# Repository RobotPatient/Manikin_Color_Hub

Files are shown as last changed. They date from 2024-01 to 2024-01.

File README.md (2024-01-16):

# Manikin_Color_Hub

Welcome to the Manikin Color Hub, a part of the skin color research team RGBbaby. 
Here's an overview of our file structure:

# Manikin Colour Hub

## Led Driver Board Files, Flexible LED Strip PCBs, and Software

Welcome to the Manikin Colour Hub, a part of the skin colour research group RGBbaby. Here's an overview of our file structure:

### Arduino Spectrometer:

Contains CAD and code files for the AS7341 colour sensor. Use this sensor setup to analyze the light emitted by a specific sample.

### General Docs:

- **Product_report - individual reports:** Individual project files included in the product report.
- **Product Report:** Detailed report on our project.
- **Progress Report:** Overview of our progress.
- **Initial Questions and Answers from WKZ:** Compilation of our initial queries and responses.
- **Manual:** Comprehensive guide for our project.
- **ToDo List:** List of tasks yet to be completed.

### Led Test Setup:

Code for testing a bare neopixel LED strip in combination with an Adafruit Feather M0 Express.

### PCBs:

- **LedDriverBoardV1:** KiCad files and schematic for the first version of our LED driver board.
- **LedDriverBoardV2:** KiCad files, schematic, code, and flexible PCBs for the second version of our LED driver board.
- **LedDriverBoardV3:** KiCad files, schematic, code, and flexible PCBs for the third and final version of our LED driver board.

### Pi Spectrometer:

CAD files for the Raspberry Pi-based spectrometer.

Feel free to explore and contribute to the Manikin Color Hub's diverse set of files and resources. 
If you have questions, reach out to us!

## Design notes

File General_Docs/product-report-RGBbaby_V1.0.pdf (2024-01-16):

# Product report – RGBbaby

By Manon Sijben, Marlon Reijlink, Emiel Visser and Joris Bol

DOCUMENT ORGANIZATIONAL DETAILS:
Document Type:
Skills Consultant: | Paul van Wegen
Project Client: | Johan Korten
Education: | Embedded Systems Engineering
Institute: | School of Engineering and Automotive, Hogeschool Arnhem-Nijmegen
Report Date: | 16-1-2023
Report Version: | v1.0
Project Duration:
Education Term:
Students: | 2108100 (Joris Bol), 2111740 (Emiel Visser), 2106573 (Manon Sijben),
| 2107003 (Marlon Reijlink)

Embedded Systems Engineering · HAN University of Applied Sciences

- please don't print this document unless you really need to!

## Version management

Version | Date | Change | Name
V1.0 | 5-9-2023 | Creation document. | J. Bol
V1.0 | 26-9-2023 | Addition C4 and introduction. (detailed history) | J. Bol
V1.0 | 10-10-2023 | Changes made to requirements. | J. Bol
V1.0 | 10-12-2023 | Added more info. | E. Visser
V1.0 | 18-12-2023 | Addition C2. (detailed history) | J. Bol
V1.0 | 18-12-2023 | Addition C4. (detailed history) | J. Bol
V1.0 | 19-12-2023 | Addition C5. | E. Visser & J. Bol
V1.0 | 9-1-2024 | Added Appendix B. | E. Visser
V1.0 | 11-1-2024 | Spellcheck, added sources, small modifications. | E. Visser
V1.0 | 12-1-2024 | Spellcheck, added sources, small modifications. | E. Visser
V1.0 | 16-1-2024 | Add conclusion, addition C6, addition summary. | E. Visser & J. Bol

## Summary

This project, conducted in collaboration with Wilhelmina Children’s Hospital for HAN University of Applied Sciences, aims to develop a realistic skin that can change appearances and respond to user input. The primary objective is to contribute to a larger initiative focused on creating a lifelike doll for nurses to practice scenarios involving premature or problematic babies.

To meet the client's specifications, a comprehensive investigation into component selection was carried out. The key focus was on choosing suitable components that could alter the skin colour of the skin and a device capable of sensing when the skin is touched. The research led to the selection of the SMDLX0707RGBTR led as the skin colour altering device and the AT42QT2120-MMHR as the touch sensing device. Two PCBs were developed to mimic the functionality of the final product during this selection process.

In order to ensure a satisfactory end result, SMART-statements were defined to guide the product development. These statements were translated into a set of functional and technical specifications, aligning with the client's vision after consultation.

Following the definition of project conditions, the physical makeup of the product and software functions were outlined, using flow diagrams and schematics. The fabrication phase commenced, utilizing ECAD software for PCB development and incorporating necessary adjustments. Once the design was finalized, PCBs and corresponding components were ordered based on the preliminary research.

Upon receiving all components and PCBs, assembly took place, and the testing phase began. Unfortunately, significant issues with the PCBs emerged, leading to an inability to upload code or generate light with the led strip. Although testing became impossible, a comprehensive testing plan for potential future projects addressing the same problem was established.

While the current PCB is at this point non-functional, the research conducted holds valuable insights for future endeavours. Recommendations to rectify the issues were identified, promising enhancements for the project's utility once implemented. Collaboration with other educational sources facilitated the creation of a realistic skin, establishing a solid foundation for future innovations in this field. Despite the current challenges, the project has laid a constructive groundwork for further developments and improvements.

## Table of contents

Version management | 1
Summary | 2
1 – Introduction | 5
2 – Preliminary research – ESE | 6
2.1 – Objective and requirements | 6
2.1.1 – Objective | 6
2.1.2 – Requirements light sources | 6
2.1.3 – Requirements touch sensors | 6
2.2 – Light sources | 7
2.3 – Touch sensors | 9
2.4 – Preselection | 10
2.4.1 – Light sources | 10
2.4.2 – Touch sensors | 10
2.4.3 – Other components | 11
2.5 – Selection tests | 13
2.5.1 – Driver board | 13
2.5.2 – FlexLeds | 14
2.5.4 – Test method | 16
2.5.5 – Tests realisation | 17
2.6 – Conclusion | 20
2.6.1 – Driver board components | 20
2.6.2 – Flexible led strip components | 20
2.6.3 – Using the spectrometer | 20
3 – Functional design | 21
3.1 – Functional design | 21
3.2 – Technical specifications | 22
3.3 – User interface | 22
3.3.1 – On board interface / heartbeat | 23
3.4 – User interfacing | 24
4 – Technical design | 25
4.1 – Architecture | 25
4.2 – Interfaces | 26
4.2.1 – Power | 26
4.2.3 – Main leds | 31
4.2.4 – Microcontroller | 33

4.2.5 – User button: | 36
4.2.6 – I2C bus components | 36
4.3 – Software | 39
4.3.1 – Main structure | 39
5 – Realization | 40
5.1 – Hardware | 40
5.1.1 – I/O diagram | 40
5.1.2 – LedDriverBoard | 41
5.1.3 – Flexible PCB | 46
6 – Testing | 49
6.1 – Functional and physical tests | 49
6.2 – Software tests | 51
7 – Conclusion | 52
7.1 – Achievements | 52
7.2 – Challenges | 52
7.3 – Recommendations | 53
7.4 – Final thoughts | 53
8 – Personal evaluation | 54
8.1 – Emiel Visser | 54
8.2 – Joris Bol | 55
Appendix A – Document history | 56
Preliminary research – ESE | 56
Preliminary research – IPO | 56
Functional design | 56
Technical design | 56
Manual: | 56
Appendix B – IO diagram | 57
Bibliography | 58

## 1 – Introduction

This project is on behalf of the Wilhelmina Children’s Hospital (henceforth this will be called: WKZ). WKZ has a department specialising in premature babies or babies with problems, it is with this department we will be working the closest. WKZ wants a doll on which nurses can practise al kind of different situations. A big part of meaningful practise is meaningful feedback, small or big changes in skin hue is a large part of that.

This rapport answers the question: how we went to work to arrive at a solution and get to a satisfying conclusion. For the development process we will be following the design steps as described in the Vmodel. WKZ does not explicitly define any conditions, which is why this project is entirely defined in collaboration.

This report is made up of seven chapters, whom all individually describe an important aspect of our project. To make it possible for us to reach a conclusion, in chapter 2 (Preliminary research – ESE) there will be a lot of questions asked and answered. In chapter 3 (functional design) the function of our product will be defined in detail. Next in chapter 4 (technical design) there will be a detailed description of all our hard- and software. Chapter 5 (realisation) describes our process and struggles during the project. You can find all the tests that were conducted in chapter 6 and the conclusion in chapter 7. Chapter 7 also contains possible improvements and recommendations.

## 2 – Preliminary research – ESE

This next section is the preliminary research we did to select the leds and other components for our PCB(s).

### 2.1 – Objective and requirements

2.1.1 – Objective
This document is meant as research for the selection of components for the final product. The form factor and other product specific attributes are not discussed here. The main topics of this sub research are the selection of led or other light emitting elements and touch sensors.

We will work as follows: First and foremost, we need to select a sizeable portion of the components according to the specifications made in the following subsections in this chapter. Secondly, a cost benefit analyse will be made, taking into account the cost, component size, ease of use and feature set of the component. The component that comes out on top will be selected. If the client decides that the aforementioned component is not sufficient, the next best option will be presented.

A physical test will be conducted later in this project, if for some reason the selected component doesn’t function according to our expectations, this document will not be updated. The final component shall be mentioned in the product report.

2.1.2 – Requirements light sources
As previously mentioned, the leds or other forms of illumination must meet certain requirements.
1. It must be as flat as possible.
2. It must be as cheap as possible.
3. It must be as simple as possible (functionality mustn’t be affected).
4. It must be as energy efficient as possible.
5. It must be a SMD (Surface Mount Device) component.
6. It must be capable of at least RGB otherwise multiple different sources must be used.
7. It mustn’t generate too much heat.

2.1.3 – Requirements touch sensors
As previously mentioned, the touch sensors must meet certain requirements.
1. It must be as flat as possible.
2. It must be as cheap as possible.
3. It must be as simple as possible (functionality mustn’t be affected).
4. It must be as energy efficient as possible.
5. It must be a SMD (Surface Mount Device) component.
6. It must be able to sense pressure through the silicone.
7. Ideally it disconnects when pressed.

### 2.2 – Light sources

Type: | Description:
Link: | 19-337/R6GHBHC-A01/2T (https://nl.mouser.com/ProductDetail/Everlight/19-337-R6GHBHC-A01-2T?qs=8cKuZ6Ok2lbHoW%2FFyZa1pA%3D%3D) (Mouser, 2023)
Disadvantages: | Large surface area
Advantages: | Small, inexpensive
Price: | €0,13
Type: | Description:
Link: | WUE 150141M1731 (https://www.reichelt.nl/nl/nl/rgb-led-smd-3528-rood-groen-blauw-270-950-230-mcd-120--wue-150141m1731-p232068.html?PROVID=2809) (Reichelt, 2023)
Disadvantages: | Quite tall, expensive.
Advantages: | Bright, small surface area.
Price: | €0,46
Type: | Description:
Link: | KAA-3528RGBS-11 (https://www.tme.eu/nl/details/kaa-3528rgbs-11/led-diodes-smd-gekleurd/kingbright-electronic/?brutto=1&currency=EUR) (TME, 2023)
Disadvantages: | Quite tall, expensive.
Advantages: | Bright, small surface area.
Price: | €1,05
Type: | Description:
Link: | RND 135-00252 (https://www.distrelec.nl/nl/smd-led-rgb-plcc-468-nm-520-nm-632-nm-rnd-components-rnd-135-00252/p/30158847?cq_src=google_ads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) (Distrelec, 2023)
Disadvantages: | Quite tall, only available in large quantities.
Advantages: | Bright, small surface area, cheap.
Price: | €0,04
Type: | Description:
Link: | ILPL-K501-RGBW-SK105-01 (https://www.distrelec.be/nl/smd-led-5050-rgbw-460nm-505nm-615nm-intelligent-led-solutions-ilpl-k501-rgbw-sk105-01/p/30308082) (Distrelec, 2023)
Disadvantages: | Large surface area, expensive.
Advantages: | Bright, very thin.
Price: | €1,24

Type: | Description:
Link: | SMD-LX0707RGB-TR (https://nl.mouser.com/ProductDetail/Lumex/SMD-LX0707RGB-TR?qs=u16ybLDytRYfAsx%252BT62puQ%3D%3D) (Mouser, 2023)
Disadvantages: | Relatively expensive.
Advantages: | Very small, doesn’t use much IO, low current consumption.
Price: | €0,66
Type: | Description:
Link: | SMLP34RGBN1W3 (https://nl.mouser.com/ProductDetail/ROHM-Semiconductor/SMLP34RGBN1W3?qs=Wj%2FVkw3K%252BMB6e39pO3qaCw%3D%3D) (Mouser, 2023)
Disadvantages: | Expensive.
Advantages: | Very thin, very small, doesn’t use much IO.
Price: | €1,26
Type: | Description:
Link: | IN-P55QDTRGBW (https://nl.mouser.com/ProductDetail/Inolux/IN-P55QDTRGBW?qs=stqOd1AaK78tLn2kfF8cBA%3D%3D) (Mouser, 2023)
Disadvantages: | Large surface area, relatively expensive.
Advantages: | Thin, bright.
Price: | €0,65
Type: | Description:
Link: | CLQ6B-TKW-S1L1R1H1TBB7935CC3 (https://nl.mouser.com/ProductDetail/Cree-LED/CLQ6B-TKW-S1L1R1H1TBB7935CC3?qs=Rp5uXu7WBW8kseQbCcO3Lg%3D%3D) (Mouser, 2023)
Disadvantages: | Large surface area, relatively expensive.
Advantages: | Comes with white element, thin.
Price: | €0,85
Type: | Description:
Link: | SK6812 (3535) (https://www.digikey.nl/en/products/detail/adafruit-industries-llc/2686/5804107?s=N4IgTCBcDaIMoGkBsAOAjGAsgSQHLZAF0BfIA) (Mouser, 2023)
Disadvantages: | Still relatively large.
Advantages: | Doesn’t use much IO, low current consumption.
Price: | €0,49
Type: | Description:
Link: | WS2812b (5050) (https://www.tme.eu/nl/details/ws2812b-b/led-diodes-smd-gekleurd/worldsemi/ws2812b-black/) (TME, 2023)
Disadvantages: | Large surface area.
Advantages: | Doesn’t use much IO, low current consumption.
Price: | €0,49

### 2.3 – Touch sensors

Type: | Description:
Link: | TL3342F260QG (https://nl.mouser.com/ProductDetail/E-Switch/TL3342F260QG?qs=6C6BR4UgC3Of90YOH%2FEXyw%3D%3D&mgh=1) (Mouser, 2023)
Disadvantages: | Relatively expensive, small actuation zone.
Advantages: | Thin, relatively high actuation force.
Price: | €0,61
Type: | Description:
Link: | TS17-48-05-YE-260-SMT-TR (https://nl.mouser.com/ProductDetail/CUI-Devices/TS17-48-05-YE-260-SMT-TR?qs=tlsG%2FOw5FFgMrmlTrPhqZw%3D%3D) (Mouser, 2023)
Disadvantages: | -
Advantages: | Super thin, large actuation zone, cheap, relatively high actuation force.
Price: | €0,26
Type: | Description:
Link: | MPR121QR2 (https://www.digikey.nl/nl/products/detail/nxp-usa-inc/MPR121QR2/2186527) (DigiKey, 2023)
Disadvantages: | Discontinued, relatively difficult to integrate.
Advantages: | Small, relatively easy to control, lots of channels, stable.
Price: | ?
Type: | Description:
Link: | AT42QT2120 (https://www.digikey.com/en/products/detail/microchip-technology/AT42QT2120-MMHR/3678702) (Mouser, 2023)
Disadvantages: | Relatively difficult to integrate.
Advantages: | Small, relatively easy to control, lots of channels, stable.
Price: | €1,59

### 2.4 – Preselection

We have seen that there are a lot of different leds and sensors that we could use. To see which ones could be the best for our use case we make a preselection by putting the aforementioned parts in decision making matrixes.

2.4.1 – Light sources
For the non-addressable led strip, we choose the 19-337C_RSBHGHC-A01_2T and the WUE_150141M173100 leds in combination with standard R, G and B 0603 leds. We decide to go with these leds because they were either relatively cheap and available or very small.
Type: | Size: | Brightness: | Price: | Controllability single led: | Controllability multiple leds: | Score:
19-337/R6GHBHC-A01/2T | 6 | 3 | 3 | 5 | 2 | 19 14 14 15 15 19 12 16 16 17 17
WUE 150141M1731 | 1 | 3 | 3 | 5 | 2
KAA-3528RGBS-11 | 1 | 3 | 3 | 5 | 2
RND 135-00252 | 1 | 4 | 3 | 5 | 2
ILPL-K501-RGBW-SK105-01 | 2 | 5 | 1 | 5 | 2
SMD-LX0707RGB-TR | 6 | 4 | 2 | 3 | 4
SMLP34RGBN1W3 | 1 | 3 | 1 | 5 | 2
IN-P55QDTRGBW | 1 | 5 | 3 | 5 | 2
CLQ6B-TKW-S1L1R1H1TBB7935CC3 | 1 | 6 | 2 | 5 | 2
SK6812 (3535) | 3 | 4 | 3 | 3 | 4
WS2812b (5050) | 2 | 5 | 3 | 3 | 4
Size | Higher is better
Brightness | Higher is better
Price | Higher is better
Controllability single led | Higher is better

Table 1 Light sources

2.4.2 – Touch sensors
Because we wanted to have a good balance between buttons and capacitive touch sensors, we chose to put all but the MPR12QR2 IC on our PCBs because this IC has been deprecated since 2015. An alternative is the AT42QT2120. We have tested the TL3342F260QG and TS17-48-05-YE-260-SMT-TR buttons on our test flex PCB and the AT42QT2120 on our final flex PCB. We decided to split up the physical buttons and capacitive buttons because we wanted to do more research on capacitive touch sensors. But we couldn’t wait any longer with the ordering of the PCBs.
Type: | Size: | Actuation force: | Price: | Controllability: | Score:
TL3342F260QG TS17-48-05-YE-260-SMT-TR MPR121QR2 AT42QT2120 | 3 4 5 5 | 2 1 5 5 | 4 5 4 2 | 4 4 3 3 | 13 14 17 15
Size | Higher is better
Actuation force | Higher is better
Price | Higher is better
Controllability | Higher is better

Table 2 Touch sensors

2.4.3 – Other components
To drive the leds (addressable and non-addressable) we needed some extra hardware to drive them properly. In this section you will find which ones we choose and why.
Function: | Type: | Size: | Feature set: | Solderability: | Footprint layout: | Price: | Controllability: | Score:
IO multiplexer | PCAL9722HNMP | 4 | 6 | 2 | 4 | 4 | 3 | 23
IO multiplexer | PCA8574D | 1 | 4 | 5 | 6 | 5 | 6 | 27
IO multiplexer | PCA8575BS118 | 5 | 6 | 3 | 4 | 3 | 6 | 27
IO multiplexer | PCA9548ABS118 | 5 | 3 | 3 | 5 | 1 | 6 | 23
IO multiplexer | PCA9670BS118 | 6 | 4 | 4 | 5 | 5 | 3 | 27
IO multiplexer | PCA9536DR | 2 | 2 | 5 | 5 | 6 | 6 | 26
PWM driver | TLC5940RHBR | 4 | 5 | 4 | 4 | 4 | 6 | 27
PWM driver | TLC5947RHBR | 4 | 6 | 4 | 6 | 0 | 6 | 26
PWM driver | TLC59401RHBR | 4 | 5 | 4 | 5 | 3 | 5 | 26
PWM driver | PCA9685BS118 | 5 | 5 | 4 | 4 | 2 | 6 | 26
PWM driver | TLC59711PWPR | 1 | 4 | 5 | 5 | 1 | 6 | 22
Flash | 25LP064A-JLLE | 4 | 6 | 4 | 3 | 2 | 6 | 25
Flash | IS25WQ040-JNLE | 2 | 2 | 5 | 3 | 6 | 6 | 24
Flash | IS25LP032D-JLLE | 4 | 4 | 4 | 3 | 3 | 6 | 24
Flash | IS25WP032D-JKLE | 4 | 5 | 4 | 3 | 4 | 6 | 26
Flash | IS25LP080DJULETR | 5 | 3 | 3 | 3 | 5 | 6 | 25
Flash | IS25LP064D-JBLA3 | 2 | 6 | 5 | 3 | 1 | 6 | 23
Flash | IS25LP064D-JKLE | 4 | 6 | 4 | 3 | 2 | 6 | 25
Flash | IS25LP040EJYLETR | 5 | 3 | 3 | 3 | 5 | 6 | 25
Flash | AT25QL641-UUE-T | 6 | 6 | 1 | 4 | 2 | 6 | 25
Flash | S25FL116K | 2 | 3 | 5 | 3 | - | 6 | 19
Microcontroller | ATSAMD21J18A-AU | 3 | 6 | 5 | 4 | 3 | 2 | 23
Microcontroller | ATSAMD21J18A-MU | 5 | 6 | 3 | 4 | 4 | 2 | 24
Microcontroller | ATSAMD21J18A-CU | 6 | 6 | 0 | 2 | 2 | 2 | 18
Microcontroller | ATSAMD21G18A-AU | 4 | 4 | 5 | 4 | 4 | 5 | 26
Microcontroller | ATSAMD21G18A-MU | 6 | 4 | 3 | 4 | 5 | 5 | 27
Buffer (as levelshifter) | SN74HCT125DR | 2 | 5 | 5 | 4 | 5 | 6 | 27
Buffer (as levelshifter) | SN74HCT125RGYR | 5 | 5 | 4 | 4 | 4 | 6 | 28
Size | Higher is better
Feature set | Higher is better
Solderability | Higher is better
Footprint layout | Higher is better
Price | Higher is better
Controlability | Higher is better

Table 3 Other components

2.4.3.1 – IO multiplexer:
To detect when a user has pressed the skin, we wanted to add buttons or other pressure sensitive devices on the flexible PCBs. To register these button presses we decided to use I2C enabled IO multiplexer.

We ended up going with the PCA9670BS because the package is very small, it had all the features we wanted, it was relatively easy to solder, and the pinout was very convenient to route out to the pins on to the connector. We also found that the price was pretty low in comparison with to the other multiplexers we selected. However, there was one issue we did not pay attention to: It doesn’t have a library.

2.4.3.2 – PWM led driver:
To actually drive the non-addressable leds, we went with a specialized PWM led driver. We settled on the TLC59401RHBR led driver. This driver is small, it has a lot of features, it’s pretty easy to solder, it’s easy to route and it’s relatively cheap.

There is, however one small problem which we found out later. This chip also doesn’t have a premade library! This is why the TLC5940RHBR scores higher. Note: We have seen people use the TLC5940 library in combination with the TLC59401RHBR. We haven’t been able to verify this though.

2.4.3.3 – Flash memory:
Because we’re using neopixels we’re going to need more flash than usual. The microcontroller we’re using has 256k of memory though, so it is probably enough. But we wanted to have the option to have more if required.

We ended up choosing the IS25LP032D-JLLE because this chip is easy to solder and has enough storage. If you find the storage size inadequate, then you can replace this chip with a different chip because the pinout is more or less standardized. Note: Check the footprint very carefully because the sizes might differ. E.g. the footprint on the PCB is WSON but there are two WSON sizes 6x5mm and 8x6mm.

2.4.3.4 – Microcontroller:
To control the leds and communicate with the chips and other modules in the baby doll we will need a microcontroller.

For the test PCB we ended up going with the ATSAMD21J18A-MU because this chip has a lot of IO, but the overall footprint is relatively small.

However, there isn’t really a good Arduino board file available for this chip. This means you will either have to use the Atmel Xplained Xpro bootloader (quite limited) or the Adafruit feather M0 express bootloader (not made for this chip but will work. Extra IO can’t be used). You can also make a custom Arduino board file, but this is quite difficult. We tried using embedded C at first, but this proved too time consuming. However, it might be a good option for you.

2.4.3.5 – Level shifter:
To translate the 3.3V output signal to a voltage the neopixel leds require we need to use a level shifter. For our development board we went with the SN74HCT125DR. This chip was used in an Adafruit development board which we found adequate for our purpose.

The only downside of this chip is that it’s quite big. This is why we went with the SN74HCT125RGYR for the ledDriverBoardV3. Same chip, different footprint.

### 2.5 – Selection tests

To accurately select the correct light sources and touch sensors we decided that we are going to make a test set up consisting of a test board with all the possible functionalities and flexible test strips with the leds and buttons.

2.5.1 – Driver board
The driver board has 3 20-pin FCC connectors of which the middle eight pins are capable of input. There is a 4th FCC connector specifically for addressable leds.

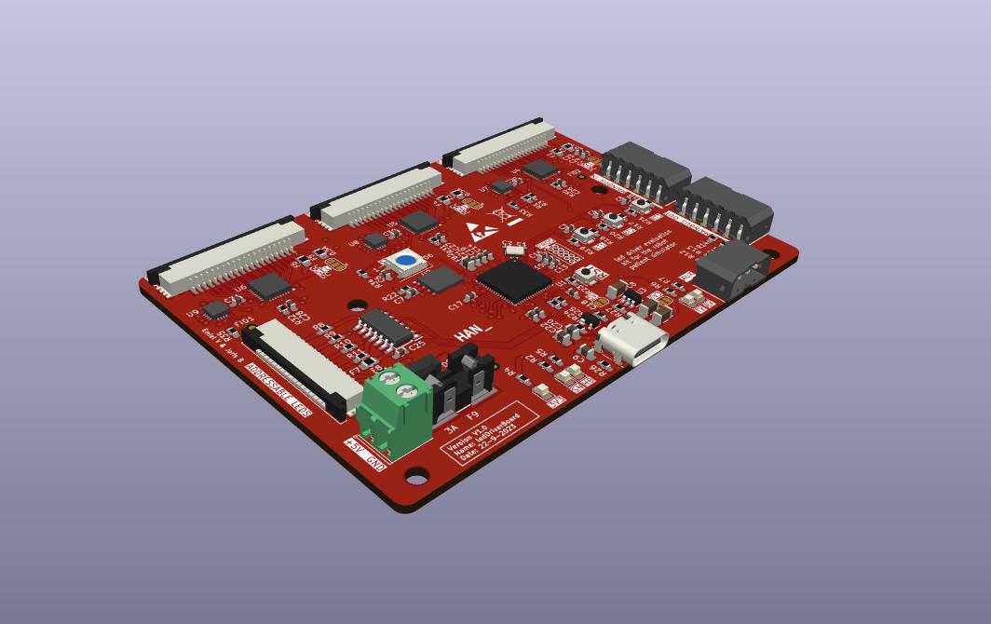
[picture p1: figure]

Figure 1 LedDriverBoardV2

This board makes use of the SAMD21J18A as microcontroller and in combination with led drivers and IO expanders the board gains a lot of functionality:

Digital interfacing
Capability: | Input/output: | Use:
3x 12-pin PWM | Output | Used to drive the normal leds.
3x 8-pin GPIO | Input/output | Used to drive the normal leds and touch sense.
4x channels for addressable leds. | Output | Used to drive the addressable leds.
debug | Input/output | Used to debug and flash the board.
Main bus in | Input | Used as the input from the mainboard.
Main bus out | Output | Passthrough.
Auxiliary | Input/output | Possibility for an extra I2C sensor.

Led functions
Colour: | State:
RGB led: Off | System is functioning normally.
RGB led: White | The PCB went into hard fault.
RGB led: Red | There is no connection between the PCB and the mainboard.
RGB led: Green | INIT finished successfully.
RGB led: Blue | The PCB is in test mode.
Heartbeat led | blinks indicating that the board is still alive.
Sens led: | Turns on when a press is detected.
3V3 led: | Is on when there is power.
Serial LEDs: | Connected to the TX and RX pins.

Button functions
Button: | Function:
RST | Resets the microcontroller.
BT1 | Can be mapped to any function.
BT2 | Can be mapped to any function.
BT3 | Can be mapped to any function.

2.5.2 – FlexLeds
The flexleds board are flexible PCBs that connect to the led driver. The two test strips that are made have the following components:

FlexLeds
Type: | Link:
Button | TL3342F260QG (https://nl.mouser.com/ProductDetail/E-Switch/TL3342F260QG?qs=6C6BR4UgC3Of90YOH%2FEXyw%3D%3D&mgh=1)
Button | TS17-48-05-YE-260-SMT-TR (https://nl.mouser.com/ProductDetail/CUI-Devices/TS17-48-05-YE-260-SMT-TR?qs=tlsG%2FOw5FFgMrmlTrPhqZw%3D%3D)
Led | SMLD12EN1WT86 (https://nl.mouser.com/ProductDetail/ROHM-Semiconductor/SMLD12EN1WT86?qs=qSfuJ%252Bfl%2Fd4fR%252B9yZydIwg%3D%3D)
Led | 19-337/R6GHBHC-A01/2T (https://nl.mouser.com/ProductDetail/Everlight/19-337-R6GHBHC-A01-2T?qs=8cKuZ6Ok2lbHoW%2FFyZa1pA%3D%3D)
Led | WUE 150141M1731 (https://www.reichelt.nl/nl/nl/rgb-led-smd-3528-rood-groen-blauw-270-950-230-mcd-120--wue-150141m1731-p232068.html?PROVID=2809)

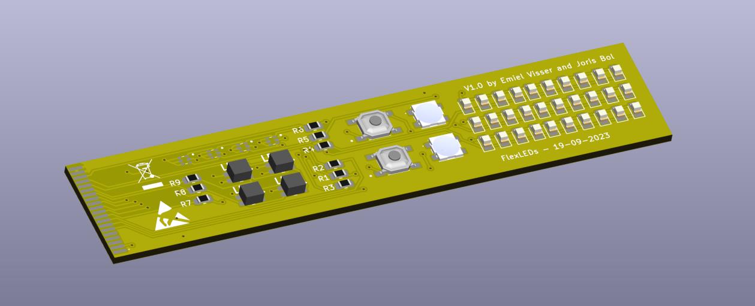
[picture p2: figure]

Figure 2 flexLeds

flexAddressLeds
Type: | Link:
Led | SMD-LX0707RGB-TR (https://nl.mouser.com/ProductDetail/Lumex/SMD-LX0707RGB-TR?qs=u16ybLDytRYfAsx%252BT62puQ%3D%3D)
Led | SMLP34RGBN1W3 (https://nl.mouser.com/ProductDetail/ROHM-Semiconductor/SMLP34RGBN1W3?qs=Wj%2FVkw3K%252BMB6e39pO3qaCw%3D%3D)
Led | SK6812 (3535) (https://www.digikey.nl/en/products/detail/adafruit-industries-llc/2686/5804107?s=N4IgTCBcDaIMoGkBsAOAjGAsgSQHLZAF0BfIA)

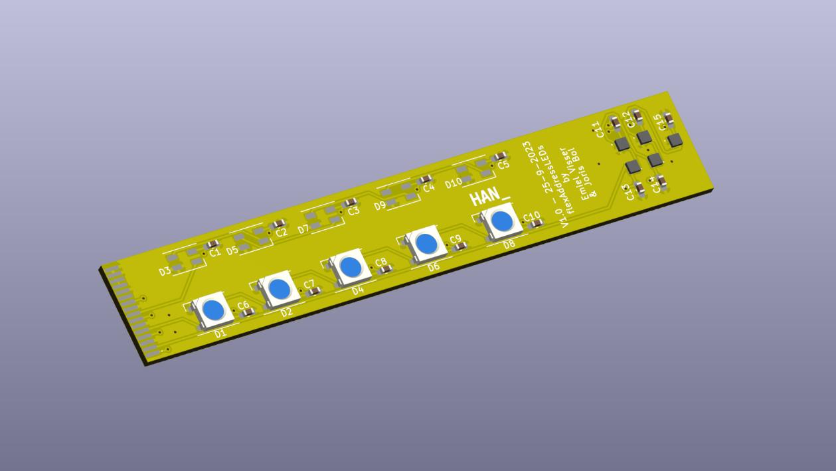
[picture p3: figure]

Figure 3 flexAddressLeds

2.5.4 – Test method
Accurate tests must be done objectively. A way to do this in our case is to measure the light intensity and the light spectrum. This can be done by using a combination of a spectrometer and a lux measuring device.

The way we intent to use these devices is as follows:

The test bench will consist of four components: the sample housing, the sensor housing, the light source, and the medium being tested. These four objects will be layered as illustrated in the figure below.

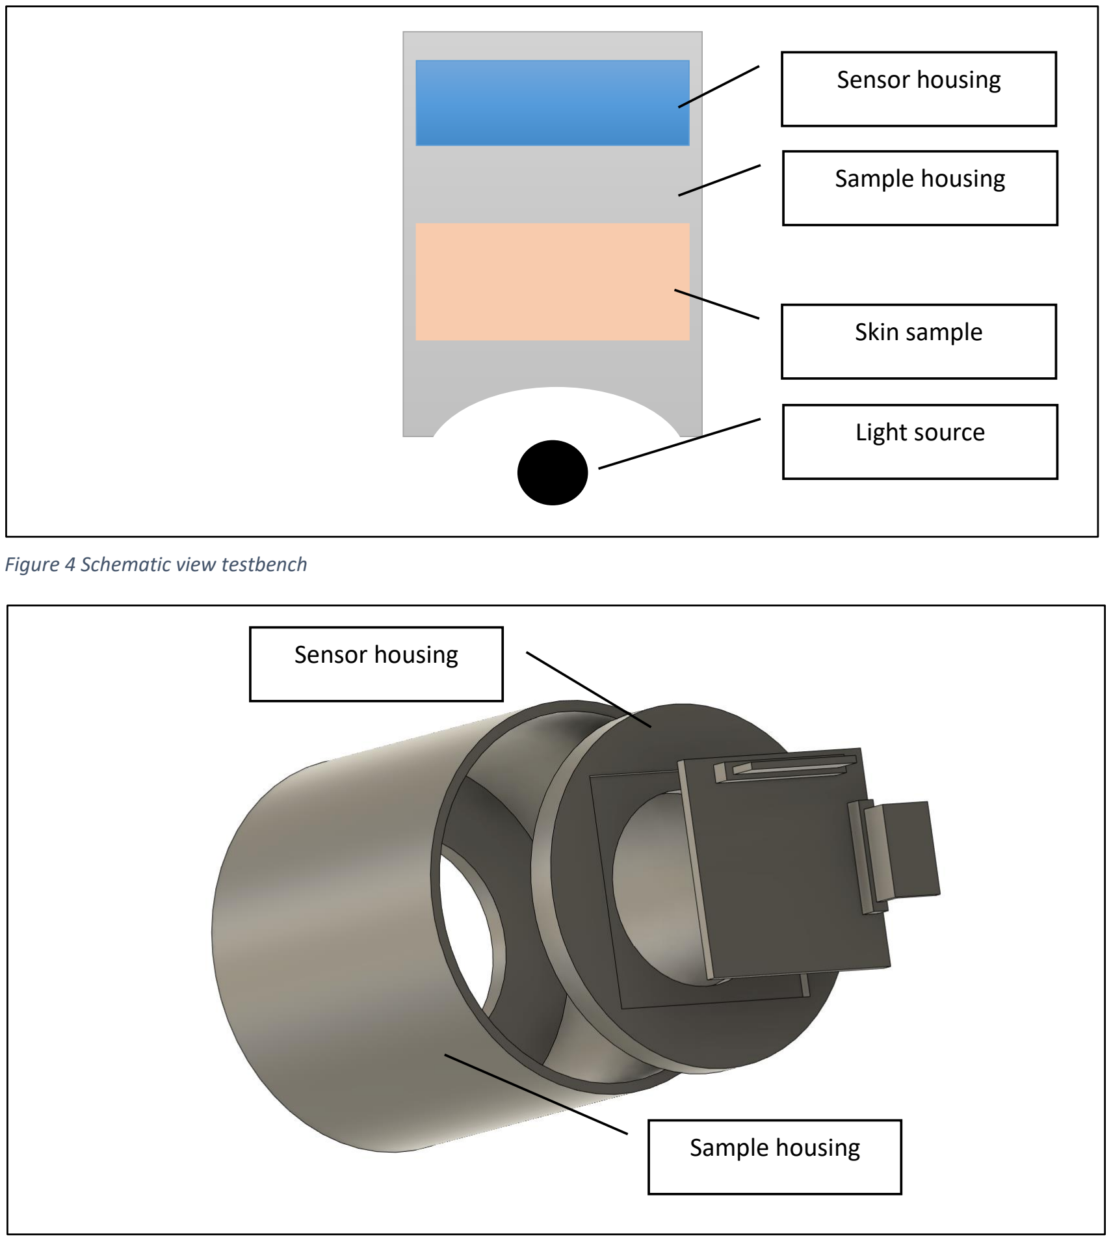
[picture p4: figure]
Figure 4 Schematic view testbench; Sensor housing; Skin sample; Sample housing; Light source

Figure 5 3D view testbench

The reason that we need to use this enclosure is to ensure that outside light is not a factor in our tests.

The components that will be used are:

- | PiCamera | (provided)
- | Spectrometer | (provided)
- | RICOH HF16HL-1b | (provided by school)
- Raspberry pi 4 or higher

For each test, the test will be conducted as follows:

1. A new sample will be put in the housing. These samples are labelled: A1, C2, etc. the samples are also labelled based on the time of production.
2. The sensor housing with the spectrometer will be lowered onto the sample.
3. The sensor and sample housing will be put on a light source.
4. The sensor value will be noted along with the sample id.
5. The sensor housing with the LUX measuring devise will be lowered on the sample.
6. Step 3 and 4 will be repeated.
7. The sample is removed from the housing.

The combination of testing and consulting will get us an objective answer on the question what colour the skin must be and what colours it must turn.

2.5.5 – Tests realisation
To conduct the test, we need to first accomplish the following steps:
1. Assemble the test board.
2. Assemble the flexible led strips.
3. Assemble the spectrometer.
4. Have working code for the spectrometer.
5. Have working code for the test board.

Each of the aforementioned points had a lot of complications and compromises, the changes that we made are all discussed in the next subchapters. At the end of this chapter, a new test plan will be established, and the coinciding tests will be carried out.

2.5.4.1 – Assembling the test board:
During the assembly end physical testing of the board, three main problems came up: the flash chip (did not line up with its footprint), the diode (that protects the board from reverse plugins) and the crystal.
- The flash chip did not correctly line up with the footprint we had chosen for the test board. At first it seemed that it did line up, but when we plugged in the test board the 3.3V led stayed of, meaning we had a short somewhere in our circuit. After some measurements we concluded that it was the flash chip end consequently removed it. This fixed the short problem.
- The diode we selected for the reverse plugin protection for the external power supply, didn’t physically fit on the board, so we bridged it and called it a day.
- The problem regarding the clock had us stumbled the longest. When we first put an Arduino bootloader on the board and noticed that nothing worked, we concluded rather quickly that it was due to the clock. But rather than fix the clock issue we tried to use bare C to program the microcontroller. This worked initially, we got some leds to blink. All the uploading, however, went via a Segger directly connected to the chip. The next step to see if our board was capable, is to see if we could get our onboard neopixel to blink. This, however, did not go as smooth as we had hoped. To use a neopixel you need to be able to generate a signal that is capable of switching H->L or L->H withing 90ns. We could not get this to work because our board was running on 8KHz instead of the 48MHz it is capable of. To remedy this, we tried to link the internal oscillators in such a way that we could generate close to 48MHz (as seen in the figure below).

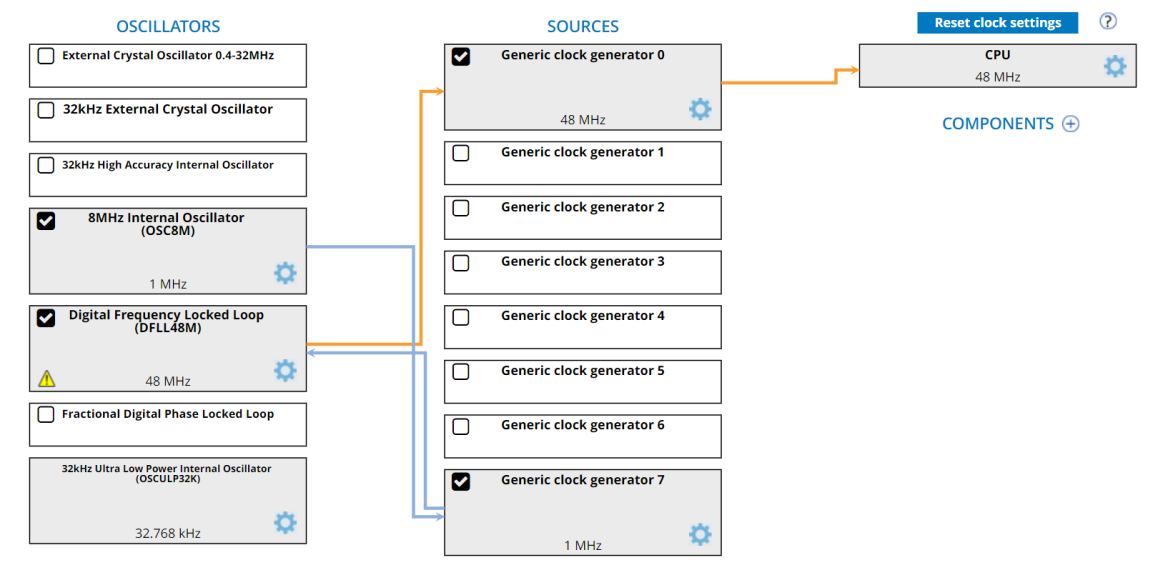
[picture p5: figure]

Figure 6 Internal clock configuration of the samd21j18a

We eventually succeeded in this and using bare C we were now capable of generating a signal with a high enough frequency. This frequency – sadly – was not capable of sustaining anything
you | could | call | stable, | so | this | also | ended | in | a | dead | end.
So we decided to combat the problem at its roots, we fixed the oscillator. The original problem was that we did not have the correct load capacitor values (C1 and C2).

2.5.4.2 – Assembling the flexible led strips:
Luckily, there weren’t a lot of problems regarding the assembly of the flexible led strips. There were however two small inconveniences. Some of the components of the led strip with the non-addressable leds came in late, so we couldn’t yet assemble them. One of the leds on the addressable led strip caused a short underneath by its pads. This however was a quick fix.

2.5.4.3 – Assembling the spectrometer:
Assembling the spectrometer was a job without too many complications. The project that we followed did not mention which raspberry pi we needed so at first, we had a pi 3 and the software did not work on it. Then we tried the pi 4 and that worked fine.

To mount the spectrometer, we had to develop a stand, shown in the figure below.

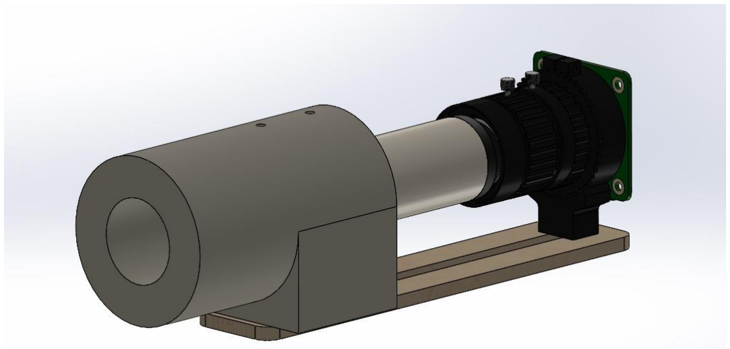
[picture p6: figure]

Figure 7 Spectrometer stand.

We assembled the spectrometer according to a process better described in the RGBbaby manual.

2.5.4.4 – Spectrometer code:
As previously mentioned, we followed a project for the spectrometer. For a more detailed inside, please refer to our manual or go directly to: https://github.com/leswright1977/PySpectrometer2 (Wright, 2023)

2.5.4.5 – Test board code:
The test board has the bootloader from the Atmel Xpro on it. This bootloader matches the SAMD21J18A pinout the best. With Arduino we can now get the leds to light up any colour we want. The previous statement only applies to the addressable leds. This is because the pins for the PWM driver don’t match up with the bootloader. This is, however, not an issue because we realised that the final product will always use some kind of addressable leds. The code that we used is from Adafruit’s neopixel lib. We can use statements like strip.fill(colour, z, n); to change the colour of the strip. This simple functionality is enough for the tests we will be conducting.

### 2.6 – Conclusion

Concluding our research, we want to achieve / know which components and methods we are going to use from now on. The things we have discovered and have the perseverance for are:

- What components we are going to use for the driver board.
- What components we are going to use for the flexible led strip.
- How future groups can use our spectrometer.

2.6.1 – Driver board components
Due to the problems, we encountered with assembling and using the test board, we will make the following changes to the newer iterations.
- We are going to use the SAMD21G18 instead of the SAMD21J18. This is due to the problems we have with addressing and using all the pins that we have available, and the fact that we don’t need as much IO.
- We dropped the support for non-addressable leds. This includes: the 20 pin FFC connector, the IO extenders, and PWM chips.

We also made some changes to existing parts of the chip, which didn’t work properly or weren’t sufficient.

- We adjusted the footprint and location of the debug connector, so it fits properly.
- The new board will support more flexible led strips.

2.6.2 – Flexible led strip components
We were able to select the ledsthat we will be using from now on. These will be the SMDLX0707RGBTR. We made this decision based on the following properties:
- They are small 0.7X0.7 inch.
- They use the same data protocol as neopixels, which is well documented.
- The don’t use a lot of power.

As for the touch detection. We tried the buttons, but they were all not able to deliver the desired result. So, we abandoned that way of detecting touch.

2.6.3 – Using the spectrometer.
The spectrometer will be more useful in later stages of this project. Sadly, we weren’t able to use the spectrometer to its fullest potential. This is why we recommend that future teams will use it. A guide can be found in our RGBbaby manual.

## 3 – Functional design

### 3.1 – Functional design

The primary function of our product is to introduce a variation in skin colours. The following list of functional requirements has been defined in consultation with our client. This list consists of three columns: The requirement number, prioritization based on the MoSCoW method and formulation of the requirement according to the SMART method.

With the MoSCoW method we can determine the importance of each specification. The M stands for must have. We must implement this specification in our final product. The S stands for should have. denoting features that are highly desirable and expected in the final product. The C stands for could have. suggesting optional features that may be considered for inclusion. The W stands for won’t have. indicating that these features won't be incorporated into the final product due to their perceived difficulty or lack of importance.

The SMART method dictates that each specification must be formulated according to the following guide rules:
- Specific: Goals should be clear and specific.
- Measurable: Goals should have measurable criteria for tracking progress.
- Achievable: Goals should be realistic and attainable.
- Relevant: Goals should be relevant to your overall objectives.
- Time-bound: Goals should have a defined timeframe or deadline.

Using the SMART method helps ensure that goals are well-defined, achievable, and aligned with your larger objectives, increasing the likelihood of success.

Functional specifications
# | MoSCoW | Description

F1 | M | The skin should be able to change colour realistically.
F1.1 | M | The skin must be able to turn yellow.
F1.2 | M | The skin must be able to turn red.
F1.2 | M | The skin must be able to turn dark blue.
F1.3 | M | The skin must be able to turn pale.
F1.4 | S | The skin shouldn’t emit a lot of light.
F1.5 | S | The skin should be able to accurately simulate petechiae. Added on 10-10-23
F2 | S | The skin should feel realistically.
F2.1 | S | The skin should not feel sticky.
F2.2 | S | The flexibility of the skin should match the flexibility of real skin.
F3 | S | The skin should look realistically.
F3.1 | S | The skin shouldn’t enter the uncanny valley*.
F3.2 | S | The colour of the skin should be realistic.
F4 | C | The skin could react to being touched.
F4.1 | C | The touched spot could display capillary refill**.
F5 | S | The system should work on different skin colours.
F5.1 | S | White skin colour.
F5.2 | S | Brown skin colour. Removed on 10-10-23
F5.3 | S | Dark brown colour. Removed on 10-10-23
F6 | M | We must test our system on different skin colours.
F6.1 | S | White skin colour.
F6.2 | S | Brown skin colour. Removed on 10-10-23
F6.3 | S | Dark brown colour. Removed on 10-10-23

*Used in reference to the phenomenon whereby a computer-generated figure or humanoid robot bearing a near-identical resemblance to a human being arouses a sense of unease or revulsion in the person viewing it.

**The 'capillary refill' time is the time it takes for colour to return to a distal capillary network after pressure has been applied.

### 3.2 – Technical specifications

The table below presents the technical specifications, adhering to the same formatting principles we applied to the functional specifications table in paragraph 1.

Technical specifications
# | Moscow | Description

T1 | M | The used microcontroller is the SAMD21J18A-M. Removed on 4-12-2023
T1.1 | M | The microcontroller must be placed on a PCB designed by us.
T2 | M | The used silicone is Eurosil 8 or 33 Transparant.
T2.1 | M | The silicone must be used to create the skin for the baby.
T2.2 | M | The silicone must not tear apart.
T3 | M | The used pigments come from NEILL’s.
T3.1 | M | X gram of pigment is used for one litre of silicone.
T3.2 | M | X gram of flocking material is used for one litre of silicone.
T4 | M | The code must be written in CPP.
T5 | S | We should make use of flex PCBs.
T5.1 | C | We could use FFC connectors.
T5.2 | C | We could use x number of buttons.
T5.3 | C | We could use leds.
T5.3.1 | S | We should supply the leds separately with power.
T6 | M | The system must be modular.
T6.1 | M | The control PCB must be detachable from the main system.
T6.2 | M | The flex PCBs must be detachable from the control PCB.
T7 | M | The control PCB must be connected to the main I2C bus to the rest of the system.
T7.1 | M | There must be two I2C ports. An input and output port.
T7.2 | M | The standard I2C protocol must be used.
T8 | M | The PCBs must be made as compact as possible.
T9 | M | The system must produce as little heat as possible.
T10 | S | The status of the PCB must be made visible to the user.

### 3.3 – User interface

A user interface (UI) serves as the medium through which a user interacts with a system or application. Examples of user interfaces include physical screens, on-screen applications, or even a basic indicator like a led, all of which enable users to engage with a machine or software.

In the following paragraph, we will detail the specific types of user interfaces we intend to use in our project, elaborate on the information they will present to the user, and outline our implementation strategy.

3.3.1 – On board interface / heartbeat
We intend to communicate vital information regarding our system's operation using six leds. These leds will serve as intuitive indicators, providing users with a clear understanding of the system's status.

In the following paragraph, we will explain the specific roles of these leds and describe how they can be effectively utilized to monitor the system's condition.

3.3.1.1 – Serial leds:
The Serial leds are designed to provide a visual representation of both the RX (Receive) and TX (Transmit) signals between the microcontroller.

These leds will be placed next to each other. We did this to maintain a good overview of the serial communication status.

3.3.1.2 – Heartbeat led:
As the name suggests, this led blinks like a heart to indicate that the board is still ‘alive.’ The led will turn on and of every second.

3.3.1.3 – Sense led:
The sense led turns on when one of the buttons is pressed. This is extremely helpful while debugging.

3.3.1.4 – RGB led:
The RGB led indicates the state of the PCB. The distinct colours indicate the following states:
Colour: | State:
Off | Nothing is wrong, PCB is off.
White | The PCB went into hard fault.
Red | There is no connection between the PCB and the main board.
Green | INIT finished successfully.
Blue | The PCB is in test mode.

3.3.1.5 – 3V3 led
The 3V3 led indicates when a 3.3 volt is present. This means that when the board is connected to power, the led turns on. This is not dependent on the chip.

### 3.4 – User interfacing

The system will interact with the user in a before specified manner, but not only the user will have impact. Our board will be largely controlled by another piece of hardware and software. This interaction is by touch in case of the user and by I2C in case of the other hardware.

A UML use case diagram is shown below, it describes what actions can be taken and how our system will react to them. In our case there are two primary actors, both depicted on the left.

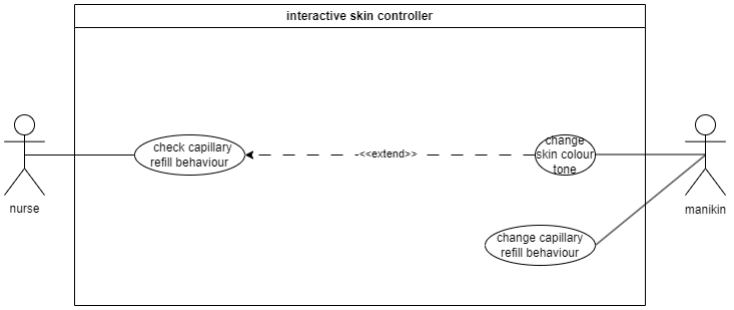
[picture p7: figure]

Figure 8 UML use case diagram

## 4 – Technical design

About the exact reason why we choose these sensors and actuators we would like to point you to our preliminary research.

### 4.1 – Architecture

In figure 1 a diagram is shown showing how our system will be controlled. The boxes contain one or more items which the board will interface with. The arrows between the boxes and board indicate the direction of the data/energy flow. The protocol/voltage is placed on the arrow.

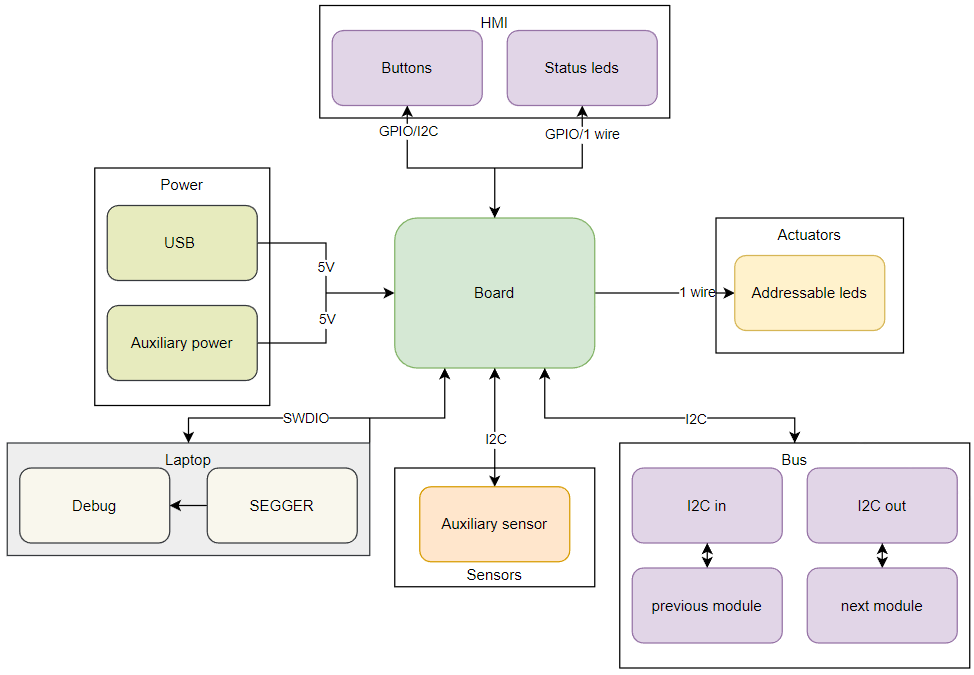
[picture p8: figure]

Figure 9 System interconnections

### 4.2 – Interfaces

In this paragraph all of the interfaces between the board and the items are described. An overview of the interfaces and items can be seen in figure 1.

4.2.1 – Power
In this paragraph the power section of our system will be described.

4.2.1.1 – USB-C:
To deliver power and upload code to our board we have added a UCB type C port to our PCB. We have added two test points so that the USB protocol can be debugged if necessary. The USB termination resistors are placed in the main sheet and are there to reduce ringing on the USB data lines. An ESD protection diode protects the host (e.g. a laptop) from ESD. The USB C port can deliver a maximum of 3A in this configuration.

Note: Don’t come close to this maximum though because the traces coming out of the port might not be able to handle 3A!

Requirement supports T7:

Specification 1.1:

No software scheme for mounting holes and fiducials.

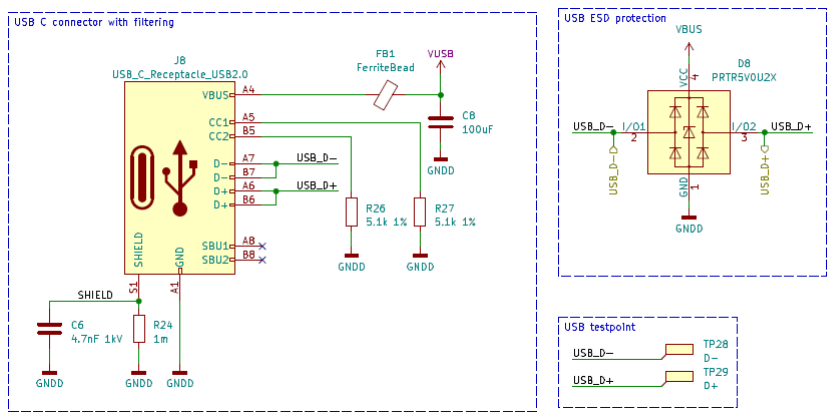
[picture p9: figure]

Specification 1.2:

4.1.1.2 – Auxiliary power:
A USB C plug can be quite bulky, so we decided to add another way of powering the system. That’s way we added a JST-XH port where 5V power can be fed into the system. We also added a fuse holder. We recommend using a fast blow fuse to protect the system in an overcurrent event.

Note: The maximum current for prolonged periods is about 2.5A. For short periods 3A is possible.

Requirement supports T7:

Specification 2.1:

No software scheme for aforementioned element.

Specification 2.2:

4.1.1.3 – 3.3V regulator:
We have decided to go with an AP2112K type regulator. This regulator drops the auxiliary and/or USB voltage down to 3.3V which is used by the microcontroller and other components. The regulator is decoupled using three decoupling capacitors and will deliver 3.3V when 5V is applied to its input.

Requirement supports T7:

Specification 3.1:

No software scheme for aforementioned element.

Specification 3.2:

4.2.2 – Status leds:
We have integrated multiple leds onto the board to provide users with clear visual indicators for various processes taking place on the controller board. These leds serve as a user-friendly interface, offering real-time feedback on the ongoing activities and status of the system.

4.2.2.1 – Status led (neopixel):
We have opted for the SK6812MINI neopixel led due to its compact package size. Additionally, these leds offer significant IO savings, a crucial factor because we decided to go with the ATSAMD21G18 instead of the original ATSAMD21J18 microcontroller. Another compelling reason for choosing this specific led is its compatibility with the existing protocol we are using for other leds. This not only streamlines our development process but also minimizes the need for additional code, promoting efficiency and consistency across our lighting system.

Requirement: supports T10

Specification 4.1:

Specification 4.2:

4.2.2.2 – HB led (heartbeat):
The Heartbeat led blinks at a fixed frequency. In the event that this led stops blinking, it indicates a system crash or that the system is stuck in a loop. Typically, a system reset is the recommended solution to address such issues.

Requirement supports T10

Specification 5.1:

Specification 5.2:

4.2.2.3 – Health led:
This led will be on when the board is in good health. And will turn of when the board encounters errors that it can’t handle properly.

Requirement supports T10

Specification 6.1:

Specification 6.2:

4.2.2.4 – Voltage indicator leds:
We've added voltage indicator leds on the board for a quick check on the availability of the two supply voltages.

Requirement supports T10

Specification 7.1:

No software scheme for aforementioned element.

Specification 7.2:

4.2.2.5 – Receive and transmit leds:
To give the user an indication if the serial bus is working, we have added a TX and RX led.

Requirement T10

Specification 8.1:

No software scheme for aforementioned element.

Specification 8.2

4.2.3 – Main leds
We have found that the SMD-LX0707RGB-TR leds fit our requirements.

Requirement T5.3

Specification 9.1:

Specification 9.2

4.2.3.1 – Neopixel output drivers:
To convert the 3.3V microcontroller output signal to a 5V output signal which results in a more stable signal. We have chosen the SN74AHCT125RGYR buffer IC. In our tests we have used the SN74AHCT125DR. the RGYR version has a smaller package which is why we went with this version for our latest revision. Every in- and output has a test point.

Requirement supports T5.3.

Specification 10.1:

No software scheme for aforementioned element.

Specification 10.2:

4.2.3.2 – FFC/FPC flat cable connectors:
To connect the flex PCBs to our control PCB we are using 16pin FFC/FPC connectors. We are using 1A resettable fuses on the 5V and 3.3V power rails. The 62-ohm resistors are there to prevent ringing on the data lines. We have also opted to breakout an I2C bus to pin 11 and 12 on the connector which enables a next group to add a I2C enabled device to be used on the flex PCBs. We also decided to breakout two IO’s to pin 8 and 9 on the connector. The user can use the for general purpose applications.

Note: The connector only makes contact on the under side so if you want your parts to be on top of the flexible PCB you need to place the connector on the underside!

Requirement T5

Specification 11.1:

No software scheme for aforementioned element.

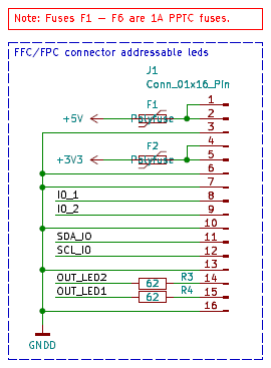
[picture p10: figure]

Specification 11.2:

4.2.4 – Microcontroller
We have chosen the ATSAMD21G18A microcontroller. This microcontroller is used by the Adafruit feather M0 express board which makes integration with Arduino or some other platform a lot easier.

Requirement T1

Specification 12.1:

The software for the microcontroller is the combination of the other specified software schematics.

Specification 12.2:

Note: The decoupling capacitors and filtering for the MCU can be found in the Power sheet of the schematic.

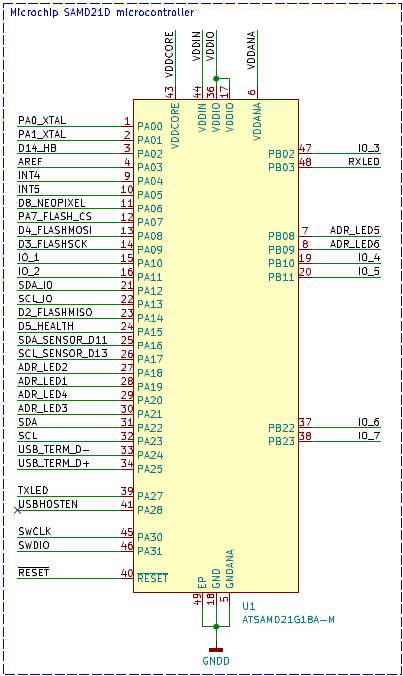
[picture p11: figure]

4.2.4.1 – Clock:
The SAMD21G18A runs on a 32.768mHz clock crystal. C1 and C2 are load capacitors. These are crucial for getting the correct clock speed. If you end up going with a different clock crystal, you will probably need te recalculate the load capacitors. The formula is in the schematic. But this formula is incorrect. For the correct formula have a look at paragraph 5.1.2. You can verify the clock speed at the test points we have placed on the clock pins.

Requirement supports T1

Specification 13.1:

No software scheme for aforementioned element.

Specification 13.2:

4.2.4.2 – Flash memory:
We are using a 64kb flash chip. The chip communicates via SPI. Every communication pin has been connected to a test point making debugging easier.

Requirement general functionality

Specification 14.1:

Specification 14.2:

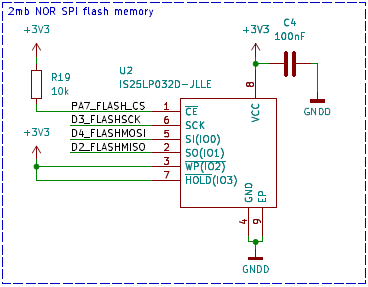
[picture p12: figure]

4.2.4.3 – Debug header:
If you want to write software to the chip (e.g. flashing a bootloader) you can use this port with a programmer like the J-LINK mini edu. This port can also be used to debug the processor and peripherals. We have added test points on the reset and data lines just in case.

Requirement general functionality

Specification 15.1:

No software functions for debug header.

Specification 15.2:

4.2.4.3 – Reset button:
To reset the system, we can use the physical reset button.

Requirement general functionality

Specification 16.1:

No software schemes for reset button.

Specification 16.2:

4.2.5 – User button:
We had one IO left so we routed that to a button. This button also has a test point.

Requirement general functionality

Specification 17.1:

Specification 17.2:

4.2.6 – I2C bus components
There are three I2C busses available. All I2C busses have test points.

4.2.6.1 – Main bus:
The main bus is the communication bus that communicates with other modules in the baby doll. The main bus has two ports. Main bus in and main bus out. You should connect the output cable of the previous module to the main bus in port on the PCB INT4 is connected to main bus in. The main bus out port connects to the next module. INT5 is connected to this port.

Requirement T7

Specification 18.1:

Specification 18.2:

5.2.6.2 – IO bus:

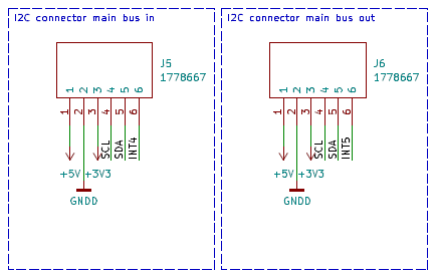
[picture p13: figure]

We wanted to maintain the possibility to add other I2C enabled devices to the flex PCBs. This is why we have broken out one I2C bus to every FFC/FPC connector. This bus also has test points.

Requirement supports T6

Specification 19.1:

See specification 18.1.

Specification 19.2:
Note: I2C output pins can be found in paragraph 4.2.3.2 – FFC/FPC flat cable connectors

4.2.6.3 – Auxiliary bus:
This bus is meant for auxiliary sensors. This bus does not have an interrupt pin connected to it and the output voltage is 3.3V only. We have used a JST-XH connector. We also added more test points tot the data pins.

Requirement supports T6

Specification 20.1:

See specification 18.1.

Specification 20.2:

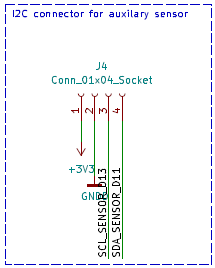
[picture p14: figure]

4.2.7 – Mounting holes and fiducials:
We have added mounting holes to the PCB the hole size is 3.2mm which means a M3 screw can be used to secure the PCB into place. The exposed copper pads near the screw hole are not connected to ground. The fiducials are positioning marks for the PCB manufacturer and pick-and-place machine.

Requirement general functionality

Specification 21.1:

No software scheme for mounting holes and fiducials.

Specification 21.2:

### 4.3 – Software

In this paragraph the software structure is described.

4.3.1 – Main structure

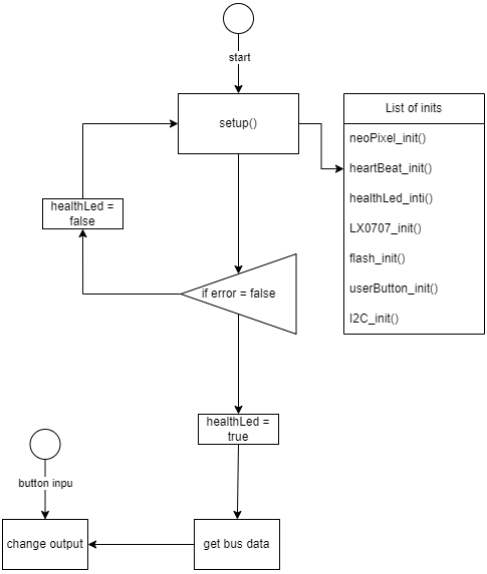
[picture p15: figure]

Figure 10 Main software structure

## 5 – Realization

In this part of the report, we describe the realisation of the project in combination with several design choices we have made to come to our final product.

### 5.1 – Hardware

In this paragraph we will describe all the hardware with relevant design choices that we have made.

We have used KiCad 7.0.9 to create the PCBs. For the 3D files we used SolidWorks 2022 and Fusion360.

5.1.1 – I/O diagram
The input/output diagram for our final PCB is listed below. In this diagram we have shown which pins are used to control the different functionalities.

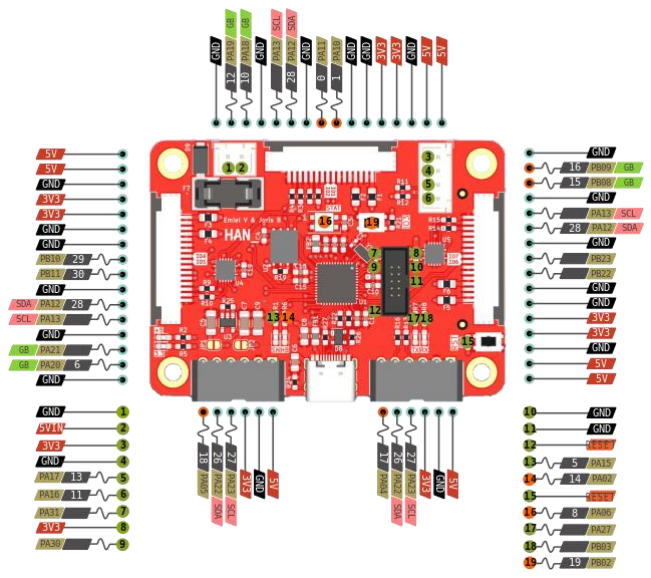
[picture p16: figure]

Figure 11 Pinout ledDriverBoardV3

For the full pin description go to: Appendix B – IO diagram

5.1.2 – LedDriverBoard
The complete schematic of the driver board for the flexible led strips is described here.

Main schematic:
In this schematic the microcontroller section is shown. We have added pullup resistors and test pads for all the I2C data busses. You can find them in the top left. The microcontroller can be found in the top middle section of the schematic. We went with the ATSAMD21G18A. As discussed in paragraph 2.4.3.4 of the preliminary research.

We have also added two buttons. A user programmable button and a reset button. These buttons have test pads as well.

If you look to the left, you’ll find the flash chip. We chose the IS25LP032D-JLLE flash chip. The reason why we chose this flash chip can be observed in paragraph 2.4.3.3 of the preliminary research.

Below the flash chip circuit, you will find the status neopixel and the USB termination resistors. The neopixel has a decoupling capacitor. It’s value can be found in the datasheet for the SK6812 led (https://www.mouser.com/datasheet/2/737/SK6812MINI_REV_01_1_2-1915201.pdf) (Mouser, 2023). The USB termination resistor values have been taken from the Adafruit feather M0 express schematic (https://learn.adafruit.com/adafruit-feather-m0-express-designed-for-circuit-python-circuitpython/downloads) (Adafruit, 2023).

Below the microcontroller you will find the mounting holes and fiducials. The mounting holes have a size of Ø3.2mm. The fiducials have no electrical purpose. They are location markings for the manufacturer.

Next to the fiducials we have placed the debug header. With this header you can debug the microcontroller and upload code or bootloaders. The pin header is a 2x5 pin header with a 1.27mm pitch.

Below that you will find the I2C bus connectors for the main bus in and out and the auxiliary connector. The Main bus in and out connectors have an extra pin connected to an interrupt enabled I/O pin. The auxiliary connector does not have this option.

Next to the auxiliary I2C connector you will find the clock circuit. You need to calculate the load capacitors for the crystal. The formula and specifications can be found in the datasheet on page 929 (https://ww1.microchip.com/downloads/aemDocuments/documents/MCU32/ProductDocuments/DataSheets/SAM-D21-DA1-Family-Data-Sheet-DS40001882H.pdf) (Microchip, 2023) and 931 (https://ww1.microchip.com/downloads/aemDocuments/documents/MCU32/ProductDocuments/DataSheets/SAM-D21-DA1-Family-Data-Sheet-DS40001882H.pdf) (Microchip, 2023)

The Clext in the formula on page 929 depends on your clock crystal, this value can be found in the datasheet of your clock crystal (https://nl.mouser.com/datasheet/2/360/file_PRODUCT_MASTER_50812_GRAPHIC03-542305.pdf) (Microchip, 2023)

The Cstray value is the capacitance of the traces going to the microcontroller and the clock circuitry in the microcontroller. This is usually around 5 or 6pF. However, the datasheet tells us that our Cstray is about 1.5pF per 12.5mm with a trace width of 0.175mm. We used a trace width of 0.25mm. The total trace length is around 8mm so a Cstray of 1.5pF should be good.

12.5pF = ([3.2pF + CLEXT] * [3.7pF + CLEXT]) / ([3.2pF + CLEXT + CLEXT + 3.7pF]) + 1.5pF

CLEXT = 18.6pF = 18 or 19pF
Note: This means the calculation and Clext (C1 and C2) in the main schematic are incorrect.

Next to the clock circuitry you will find the leds for the power indication, the TX and RX indicator leds, the heartbeat and health leds.

Above the led and clock section you will find a section with touch pads. These pads are connected to most of the IO pins and other data lines.

Above the test pad section, you will find the three FFC/FPC connectors which will connect the flexible PCBs to the mainboard. We added two I/O pins to each of the three FFC/FPC connectors. You can do whatever you want with them. We also connected an I2C bus to each of the three connectors, more on that later. The connector also has two led channels connected to it which you can use for addressable leds. Note: The led channels are 5V out!

The connectors have two 5V and two 3.3V power lines. These power lines have a 1A PPTC fuse on them. Note: Don’t run all led channels at their maximum current. The fuse will blow.

The next two squares are the power and led driver sheets. See the next paragraph.

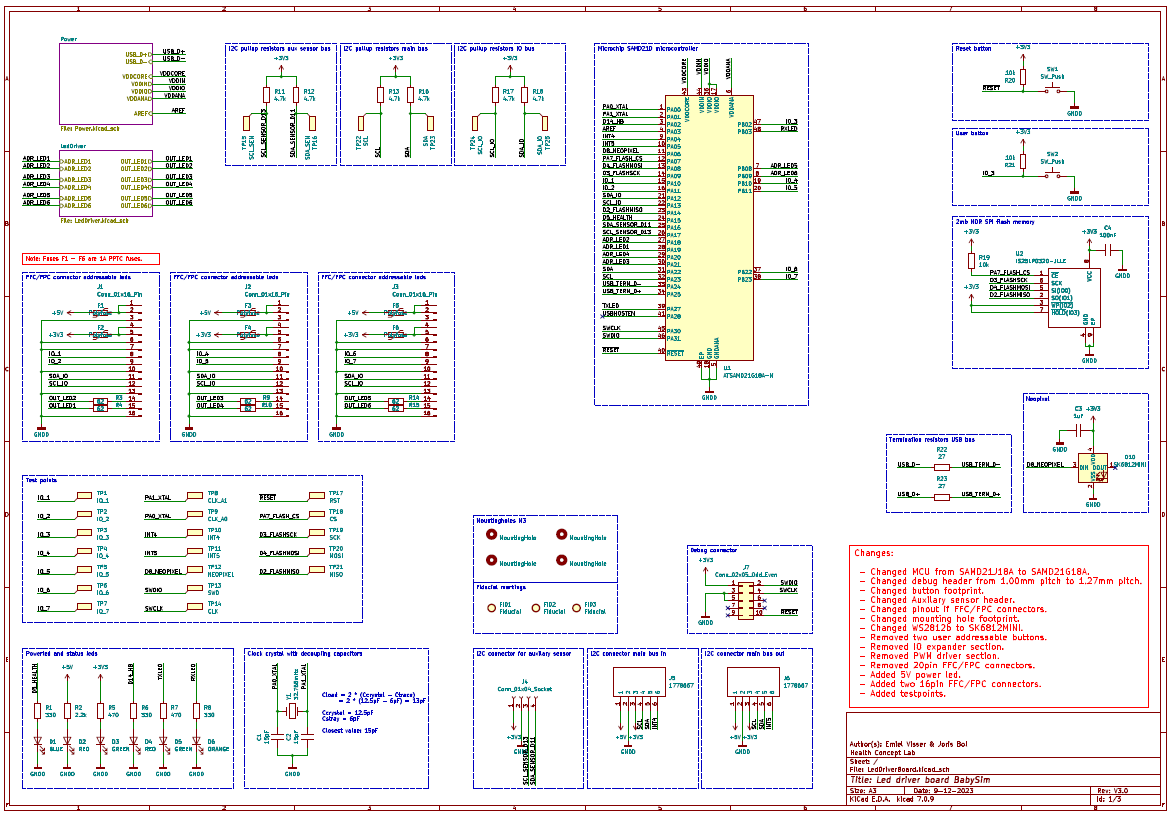
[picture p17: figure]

Figure 12 Main schematic

Power schematic:
We choose to go with a USB-C connector because the EU has begun to make the USB-C connector a legal requirement in portable devices. To make our design compliant with upcoming EU regulations, more futureproof, repairable, and thus more sustainable we decided to include this connector in our design. We added some filtering on the VUSB line. The incoming voltage is 5V@3A max. Next to the USB port circuitry you will find the ESD protection diode for the USB voltage and data lines. We also added two test points to the USB data + and USB data lines.

In this schematic you will also be able to find the decoupling capacitors for the microcontroller.

The auxiliary in connector has a 3A fast blow fuse. You can connect an external 5V power source to this connector. There is another test point connected to the connector.

The USB power lines, and Auxiliary power lines connect to the AP2112K-3.3 low dropout regulator (LDO) this LDO converts the 5V voltage to 3.3V. Be aware that the maximum output current of the LDO is about 600mA. We have added two more test points. One for 5V and one for 3.3V.

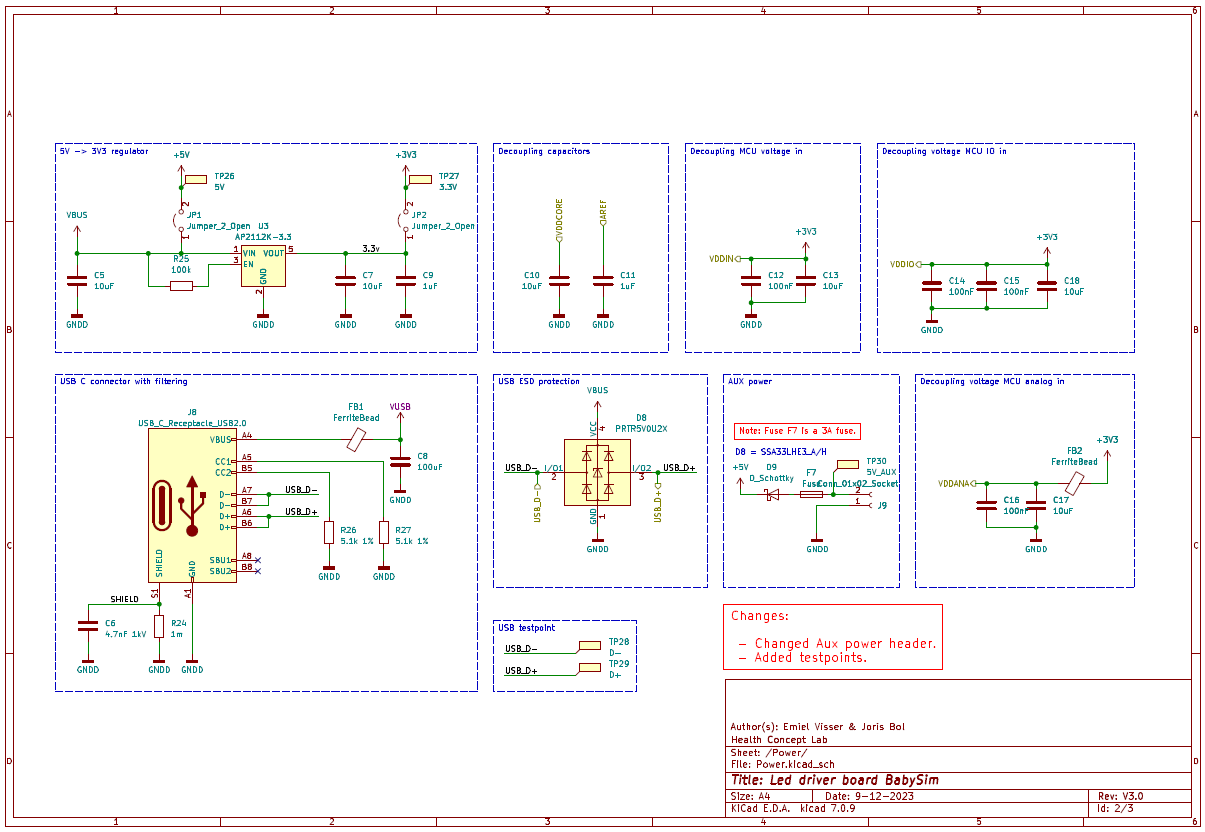
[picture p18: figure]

Figure 13 Power schematic

Led driver schematic:
In this schematic you will find the gate buffers (level shifters if you will) for converting the 3.3V led data signal to 5V. We have used the SN74AHCT125RYGR chip for this purpose. If you would like to know why we chose this particular chip. Have a look at our paragraph 2.4.3.2 of the preliminary research.

All input channels and output channels have test points on them just in case you need them.

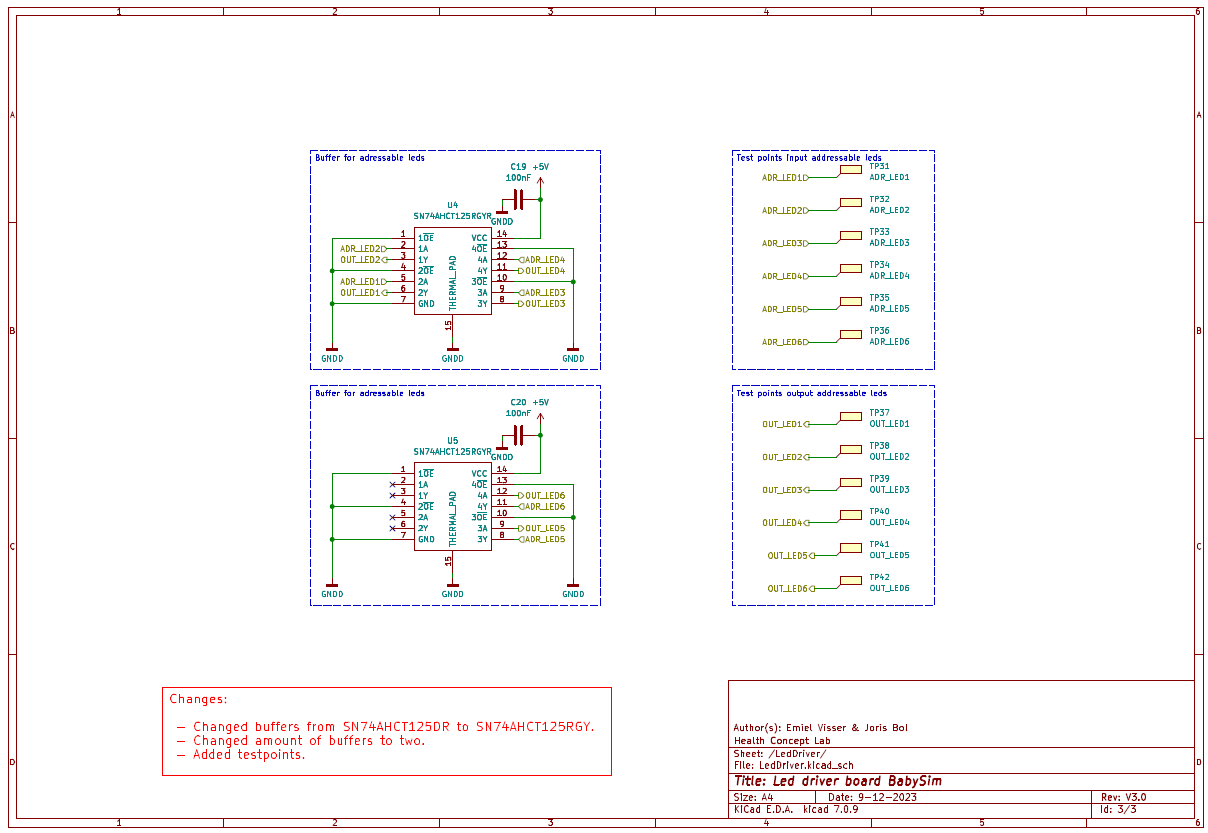
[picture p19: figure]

Figure 14 Led driver schematic.

LedDriver PCB:
Creating the layout for a PCB is always one of the hardest parts of creating a PCB design. We began by creating subgroups of components. After that we started placing the components in the subgroups in the correct orientation. We began by placing them in the PCB area. By doing this you quickly get a sense of scale.

After we had done this, we started routing the subgroups. Then we improved the component placement and updated the placement of some of the components in the subgroups. After everything was routed, we started adding the labels and logos.

For the PCB stack up we decided to go with a four-layer design. By doing this we gain a lot more room to route te traces. Going with this particular layer stack up also gives us more signal stability.

The stack up is as follows:

Layer: | Net name:
F.Cu (front) | Signal/Ground.
In1.Cu | Ground.
In2.Cu | Power 3.3V/5V.
B.Cu (Back) | Signal/Ground.

We tried to make the In1 and In2 layers a power and ground only layer, but we ended up having to route a couple of traces on these layers as well.

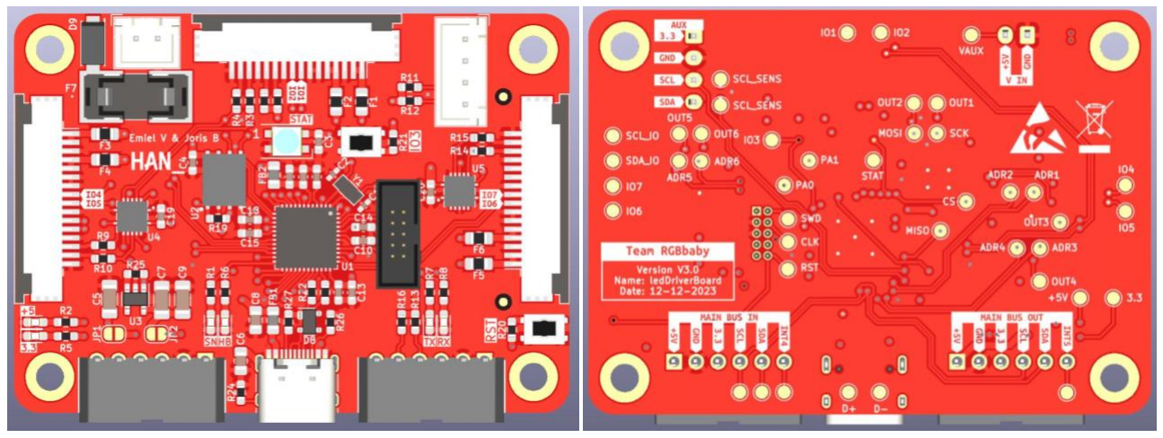
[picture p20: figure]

Figure 16 Driver board front | Figure 15 Driver board back

5.1.3 – Flexible PCB
This paragraph describes the function and considerations made during the design and assembly of the flexible PCB. This PCB is responsible for the colour changing capabilities of the skin we developed. It also contains the capability to sense touch, using a capacitive touch chip and pads. This particular part of the PCB is still in its testing face and has not been proven.

The flexible PCB consists of four main parts:

- The connector.
- The leds.
- The capacitive touch chip.
- Touch pads (which are not visible on the figure below.)

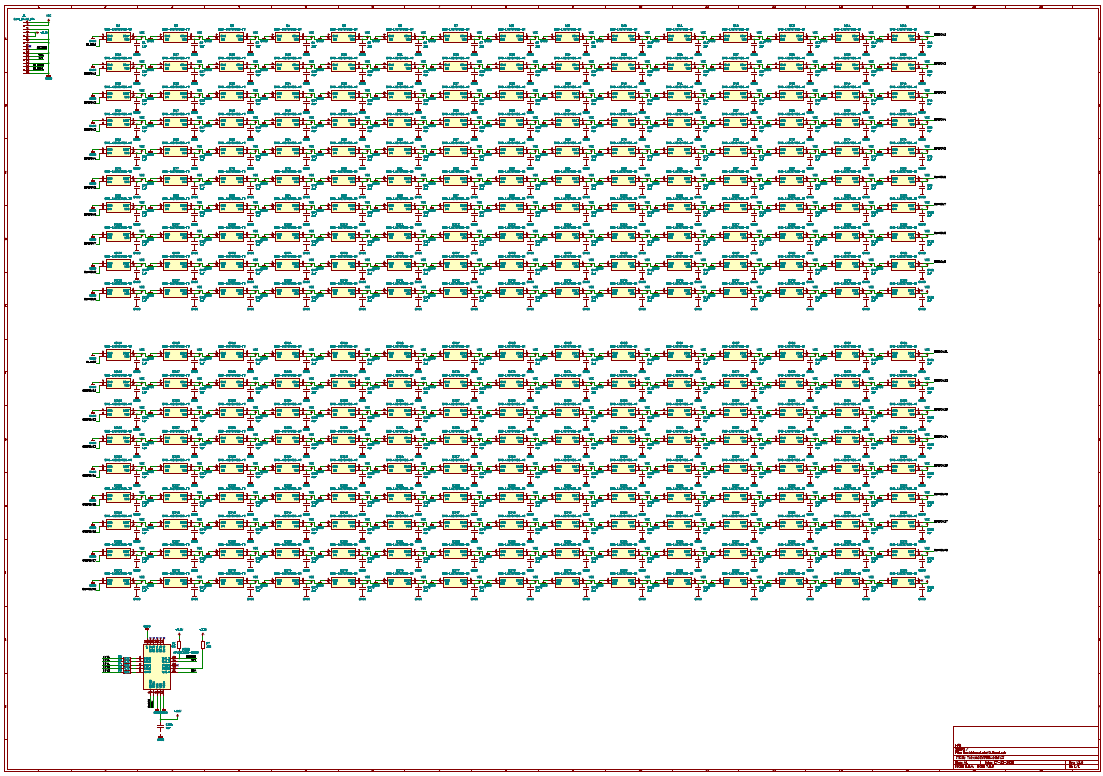
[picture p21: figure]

Figure 17 Main schematic

The connector:
The connector of the flexible PCB is not a component but rather the PCB itself. It must fit in a FFC connector, which is present on the driver board. To successfully make a piece of the PCB function as a connector we had to add traces in the correct place, and we needed to add a stiffener, so the connector does not bend or rip. The measurements and connection are depicted in the figures below.

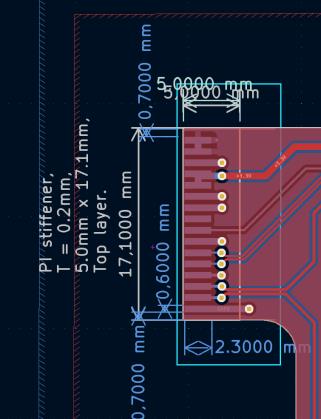
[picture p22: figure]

Figure 18 Connector schematic | Figure 19 Connector layout

The leds:
As sufficiently explained in paragraph 2.6.2, we choose the SMDLX0707RGBTR leds. these are present on the PCB in great number. The led grid contains 15 X 19 leds. this totals 285 leds. they are arranged in such a way that the leds are spaced 3,9mm centre to centre. This came out of our tests as a small enough gap, so the leds don’t cause spotting.

The leds are connected in such a way that it snakes down, starting at the left. The first 150 leds are driven by one IO pin and the other leds by another. This is because we were worried that driving all 285 leds with one io pin would exceed the maximum amount of ram we have available.

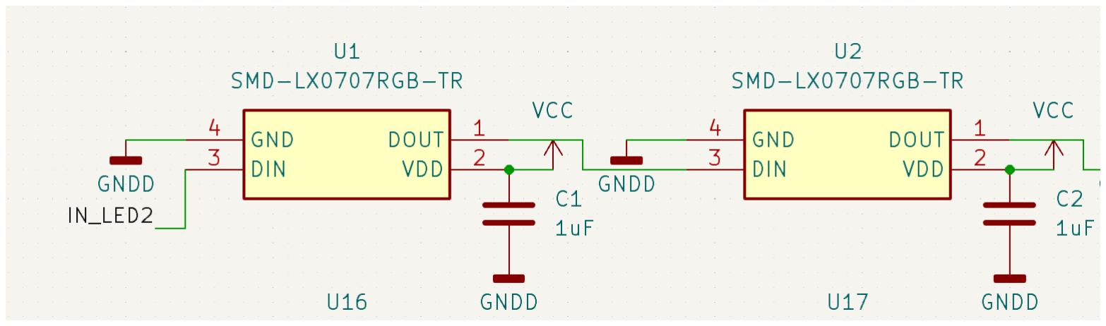
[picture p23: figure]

Figure 20 leds schematic

The capacitive touch chip:
The capacitive touch chip, which is the AT42QT2120-MMHR, is capable of sensing touch via the capacitive properties of touch. Have a look at paragraph
2.4.2 in the preliminary research to find our requirements
for the touch sensor.

It has the capabilities to run in two modes: standalone mode and comms mode. We use comms mode because we want to be able to communicate with the chip via I2C. This enables us to read the state of registers rather than relay on the multiple out channels of the chip.

We use six pins for detecting touch. Five of the pins function as a key. These keys are capable of sensing direct touch, consequently, you need to put your finger directly on the pads. The other pin is something called a prox key.
This pin – in contrast of the other keys – is capable of
sensing distance to your finger.

There is also a guard pin, which is responsible for protecting the pads for interference, more about this subject can be found in the next paragraph.

Touch pads:
The pads are responsible for supplying a surface with which you can interact. As previously mentioned, there are six pads. Five of which are keys, and one is a prox pad.

It is important to sufficiently protect the pads of interference, because of its fragile nature. We do this by using the guard channel and a ground plain.

The guard channel combats the noise that is present on the pads by putting the reverse of the interference on the guard channel. The guard channel raps around the pads so it can adequately protect them.

The ground plain is at the back side of the pads. For the pads to work correctly, there must be a precise reference point, from which the chip can derive the capacitive difference. A perfect 0V is ideal for this, hence the ground plain.

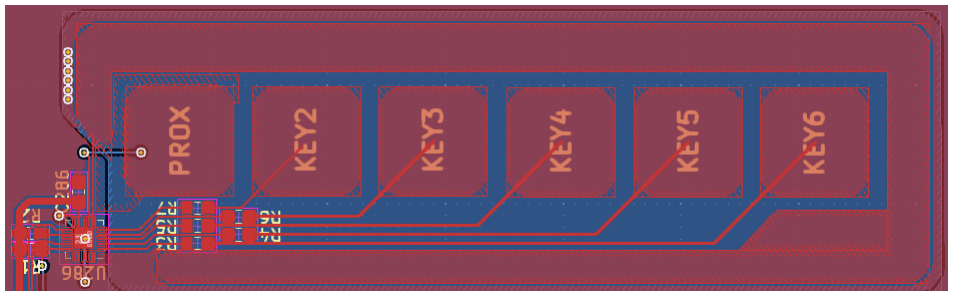
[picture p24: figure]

Figure 22 pad layout

Figure 21 Capacitive touch chip

## 6 – Testing

In this chapter we will describe the testing process and our findings. This will be done with the help of a testing method which will be described in its respective paragraph.

### 6.1 – Functional and physical tests

The Action/input variable of the test are determent by the functional an technical specifications.

Project name: RGBbaby | Date: -
Test case ID: 001 | Name: -

Function/module/program under test:

Main PCB

Test | Action/input | Expected result | Pass/Fail | Actual result
1. | The PCB turns on. | The PCB can successfully turn on. | pass | -
2. | 3V3 is available. | When 3V3 is available the corresponding led turns on. | pass | -
3. | 5V is available. | When 5V is available the corresponding led turns on. | pass | -
4. The heartbeat led is | used. | When the PCB is on the heartbeat led turns on and of with the frequency of 1Hz | - -
5. | The serial leds are used. | The serial leds turn on when there is serial communication. | - -
6. | The sense led is used. | The sense led turns on when a button is used ore when the skin senses touch. | - -
7. | The RGB led is used. | The RGB led is capable of simulating the following behaver: | - -
Colour: | State:
Off | Nothing is wrong, PCB is off.
White | The PCB went into hard fault.
Red | There is no connection

| between the PCB and the main board.
Green | INIT finished successfully.
Blue | The PCB is in test mode.
8. The PCB uses the main | I2C bus. | The PCB is capable to use the main I2C bus to read and write data. | - -
9. The PCB can generates | the data signal for the addressable leds. | The PCB can successfully generate the data signal for the addressable leds. | - -
10. The PCB supplies the | led strip with sufficient power. | The PCB can successfully supply 5V and 3V3 to the led strip. | - -
11. The PCB acts upon the | input of the led strip. | The PCB is capable of acting upon the input of the led strip, which is generated by the sense chip. | - -
Project name: RGBbaby | Date: -
Test case ID: 002 | Name: -

Function/module/program under test:

Flex PCB

Test | Action/input | Expected result | Pass/Fail | Actual result
1. The leds make the skin | turn yellow. | The skin turns a realistic yellow, without becoming a light beacon. | - -
2. The leds make the skin | turn red. | The skin turns a realistic red, without becoming a light beacon. | - -
3. The leds make the skin | turn dark blue. | The skin turns a realistic dark blue, without becoming a light beacon. | - -
4. The leds make the skin | turn pale. | The skin turns a realistic pale, without becoming a light beacon. | - -
5. One of the touch pads is | activated by a user. | We can detect and use the input of the user. | - -

6. The proximity pad is
activated by a user.

We can detect and
measure the user input.

It may be apparent that the test are incomplete and lack conclusions. This is because of the technical issues we encountered. These issues are further described in the conclusion of this rapport.

### 6.2 – Software tests

Due to the technical complications mentioned in the conclusion. We were not able to supply a sufficient software testing plan and its corresponding conclusions.

## 7 – Conclusion

Our goal was to create a solution for inducing a colour change and touch in the skin of a baby CPR doll. Our objectives included making a test setup for the components and solutions we wanted to test, writing code for controlling the driver board and documenting our findings.

### 7.1 – Achievements

Testing:
We have done a lot of research on led driving and touch sensing options. Our findings can be reused for future projects.

Hardware:
We have created a test PCB that allowed us to test different hardware and software configurations. With the lessons we learned from that test PCB we created our final PCB. This PCB has six led channels capable of driving leds up to 1A per connector. Each connector has an I2C connection so that a capacitive touch sensor can be used.

Software:
We have written a software library that makes the implementation of the led channels, IO and touch sensor a lot easier.

### 7.2 – Challenges

We have encountered a lot of hurdles, slowing us down. This is the reason why we haven’t been able to finish the project completely.

Microcontroller:
The microcontroller we had chosen for our first test board had no Arduino implementation in our configuration which meant we weren’t able to use every functionality we wanted to try out.

Clock:
On both boards we have/had problems with the onboard clock. The clock crystal needs to put out a clock frequency that is within the 32.768kHz range. However, it refused to do that on both boards which wouldn’t allow the code to be run using the Arduino bootloader because the Arduino bootloader uses the external clock instead of the internal clock circuitry. On our test board we manged to fix this by changing the load capacitors to a different value. However, this wouldn’t work on the final version.

Programming:
Because the clocks wouldn’t work we had to program in embedded C/C++. Creating libraries for the different chips is very time consuming which is what brought us into trouble. We were also unable to find a suitable Arduino bootloader for the test PCB which meant we couldn’t use a lot of the functions we wanted to test.

We also wired up the debug header to the final PCB incorrectly which meant we had to solder jumper wires to pads on the back to be able to program it.

Shorts:
We also had a number of shorts on both boards and on our led strip due to an excess amount of solder paste resulting in bridges, which took a lot of time to solve those.

### 7.3 – Recommendations

Clock:
For the final PCB to function properly, your initial priority should be getting the clock up and running. Once that's sorted, you should be able to upload the Arduino code through the USB port. Establishing a stable clock is crucial as it forms the foundational step toward ensuring the functionality of the final PCB.

Fix short:
If you want to use the flexible led strip you will need to fix the short on 5V first.

Test code:
Because of the clocking issue and the shortage of time, we haven't had the chance to test the code we wrote for the LEDs and the touch sensor.

Debug header pinout:
If you find yourself in the process of designing a new flexible PCB, it would be advisable to check and alter the pinout arrangement of the debug header on the final PCB. Taking this step could prove beneficial in optimizing the functionality and compatibility of the overall design.

### 7.4 – Final thoughts

In conclusion, our technical project focused on enhancing the functionality and realism of a baby CPR doll by incorporating a capacitive touch sensors and a subdermal lighting system. The integration of these features not only elevates the overall user experience but also addresses the critical need for realistic training simulations in infant CPR scenarios. The tactile feedback provided by the capacitive touch sensors, combined with the subdermal lighting system that simulates physiological responses, creates a training environment that closely mirrors real-life situations. This innovation holds great promise in advancing the effectiveness of medical training, ensuring that practitioners develop the necessary skills and confidence to respond to emergencies involving infants. As we reflect on the journey of this project, we take pride in contributing to the advancement of healthcare education and ultimately, the improvement of infant CPR practices.

## 8 – Personal evaluation

In this paragraph, we will share our individual perspectives and insights regarding the project.

### 8.1 – Emiel Visser

Being a part of the team responsible for creating the PCBs was a great learning opportunity for me, and I genuinely enjoyed the experience. Despite the challenges that came with having a significant role in the project, it was a bit stressful at times. However, overcoming those challenges and contributing to the team effort added a sense of accomplishment that made the whole journey worthwhile.

Personal learning goals:
In setting my personal learning goals for this semester, I aimed to achieve a better work-life balance by reducing the time dedicated to school-related tasks. Last year, I found myself putting in 70-hour weeks, and I'm pleased to report that this semester, I successfully managed to cut it down to 50 hours per week. It's a significant improvement, and I consider this goal accomplished.
Another objective was to enhance my skills in PCB design. While I did make notable progress and acquired valuable insights, I acknowledge that there is room for further development in this area. I'm satisfied with what I've learned so far, but I'm eager to delve even deeper into PCB design in the future.

Contributions:
Throughout the project, I assumed the responsibility of designing both the test PCB and the final PCB. Additionally, I took a lead role in developing the majority of the software for the final PCB. As a natural extension of these tasks, I also undertook the responsibility of crafting comprehensive documentation for both the test PCB and the final PCB, capturing the intricacies of the design and software aspects. This holistic involvement allowed me to contribute not only to the technical implementation but also to the clarity and thoroughness of the project documentation.

Conclusions:
I must admit that I significantly underestimated the scope and complexity of this project. However, as I immersed myself in the tasks and challenges it presented, I found immense satisfaction and fulfilment in the work. The journey not only exceeded my expectations but also became a source of profound learning. The diverse experiences encountered throughout the project provided valuable insights, and overcoming the initial underestimation became a pivotal aspect of my personal and professional growth.

### 8.2 – Joris Bol

This project helped me to become more of a team player. This multidisciplinary project helped me develop my communication skills better and made me more aware of how other people function. I found this a most enjoyable experience, besides the work it sometimes created. I think of this project as overall a positive encounter.

Personal learning goals:
The goals that I want to achieve this semester were to introduce myself to PCB design and to get better at English report writing. For both of these goals there wase tremendous opportunity withing this project. I was able to get acquainted wit ECAD software and because of the main language within this project, I was forced to exercise my English skills. I would like to say that I was more than moderately successful, improving my English skills substantially and going beyond just the beginning of ECAD.

Contributions:
Due to my personal goal of learning the basics of ECAD we created an opportunity for me to develop three PCBs. Because of my involvement with the development of these PCBs and the debugging there of I was able to succeed in my second learning goal: writing documentation. Documentation and research were one of the biggest parts of this project, making up for at least 50% of the time I spend on this project. A large part of documentation was making it so that future projects had something to build upon, and I like to think that I was of help in that matter.

Conclusions:
This project is something I always wanted to do. From an early age I knew I wanted to do something withing the health sector in combination with technology. The assignment we did fell perfectly within these interests. I must admit that I found this project harder than I anticipated, this was mostly caused by the uncertainty of what to do in the beginning and my inexperience with some of the technologies we used. I did however find it an enjoyable project from which I learned a lot.

## Appendix A – Document history

### Preliminary research – ESE

Version: | Date: | Change: | Name:
V1.0 | 5-9-2023 | Creation document and C1. | J. Bol
V1.0 | 26-9-2023 | Addition of C4 and improvement of C2 and C3. | E. Visser & J. Bol
V1.0 | 2-10-2023 | Spellcheck and added extra info. | E. Visser
V1.0 | 9-12-2023 | Added info. | E. Visser
V1.0 | 10-12-2023 | Added info. | E. Visser
V1.0 | 12-12-2023 | Finished chapter 5 | J. Bol
V1.0 | 13-12-2023 | Added decision making matrixes. | E. Visser
V1.0 | 14-12-2023 | Added more decision-making matrixes. | E. Visser
V1.0 | 17-12-2023 | Added component explanations. | E. Visser
V1.0 | 18-12-2023 | Added conclusion | J. Bol

### Preliminary research – IPO

No history available

### Functional design

Version | Date | Change | Name
V1.0 | 5-9-2023 | Initial setup | J. Bol
V1.0 | 9-9-2023 | Added information | E. Visser
V1.0 | 11-9-2023 | Added information | Everybody
V1.0 | 12-9-2023 | Added information | J. Bol & E. Visser
V1.0 | 26-9-2023 | Added UML. | J. Bol
V1.0 | 1-10-2023 | Spellcheck. | E. Visser
V1.0 | 12-12-2023 | Added changes. | E. Visser

### Technical design

Version: | Date: | Change: | Name:
V1.0 | 5-9-2023 | Creation document. | J. Bol
V1.0 | 17-9-2023 | Added paragraphs. | E. Visser
V1.0 | 16-10-2023 | Added info. | E. Visser
V1.0 | 27-11-2023 | Added info. | E. Visser
V1.0 | 1-12-2023 | Added info. | E. Visser
V1.0 | 9-12-2023 | Added info. | E. Visser
V1.0 | 10-12-2023 | Added info. | E. Visser
V1.0 | 18-12-2023 | Added info. | J. Bol
V1.0 | 16-1-2024 | Spellcheck. | E. Visser

### Manual:

Version: | Date: | Change: | Name:
V1.0 | 11-9-2023 | Creation document, preface, C1, C2 & C3. | J. Bol
V1.0 | 12-11-2023 | Added programming environment tab. | E. Visser
V1.0 | 20-11-2023 | Added spectrometer tab. | J. Bol
V1.0 | 04-01-2024 | Added more information in the hardware section. | E. Visser
V1.0 | 05-01-2024 | Added more information in the hardware section. | E. Visser
V1.0 | 06-01-2024 | Added more information in the hardware section. | E. Visser
V1.0 | 07-01-2024 | Added info in the hardware and debugging section. | E. Visser
V1.0 | 09-01-2024 | Added bibliography, performed spellcheck. | E. Visser

## Appendix B – IO diagram

Microcontroller: | Pin on microcontroller: | Schematic name: | Function:
ATSAMD21G18A-M | PA00 | PA0_XTAL | Oscillator pin 0
ATSAMD21G18A-M | PA01 | PA1_XTAL | Oscillator pin 1
ATSAMD21G18A-M | PA02 | D14_HB | Heartbeat led
ATSAMD21G18A-M | PA04 | INT4 | Interrupt main bus in
ATSAMD21G18A-M | PA05 | INT5 | Interrupt main bus out
ATSAMD21G18A-M | PA06 | D8_NEOPIXEL | Status neopixel led
ATSAMD21G18A-M | PA07 | D4_FLASH_CS | Chip select pin flash chip
ATSAMD21G18A-M | PA08 | D4_FLASHMOSI | Mosi pin flash chip
ATSAMD21G18A-M | PA09 | D3_FLASHSCK | Clock pin flash chip
ATSAMD21G18A-M | PA10 | IO_1 | General purpose input/output pin FFC connector
ATSAMD21G18A-M | PA11 | IO_2 | General purpose input/output pin FFC connector
ATSAMD21G18A-M | PA12 | SDA_IO | I2C datapin FFC connector
ATSAMD21G18A-M | PA13 | SCL_IO | I2C datapin FFC connector
ATSAMD21G18A-M | PA14 | D2_FLASHMISO | Miso pin flash chip
ATSAMD21G18A-M | PA15 | D5_HEALTH | Health led
ATSAMD21G18A-M | PA16 | SDA_SENSOR_D11 | I2C datapin auxiliary sensor
ATSAMD21G18A-M | PA17 | SCL_SENSOR_D13 | I2C datapin auxiliary sensor
ATSAMD21G18A-M | PA18 | ADR_LED2 | Addressable led channel 2
ATSAMD21G18A-M | PA19 | ADR_LED1 | Addressable led channel 1
ATSAMD21G18A-M | PA20 | ADR_LED4 | Addressable led channel 4
ATSAMD21G18A-M | PA21 | ADR_LED3 | Addressable led channel 3
ATSAMD21G18A-M | PA22 | SDA | I2C datapin main bus
ATSAMD21G18A-M | PA23 | SCL | I2C datapin main bus
ATSAMD21G18A-M | PA24 | USB_TERM_D- | USB data minus
ATSAMD21G18A-M | PA25 | USB_TERM_D+ | USB data plus
ATSAMD21G18A-M | PA27 | TXLED | TX led
ATSAMD21G18A-M | PA28 | USBHOSTEN | USB hoste enable (NOT CONNECTED)
ATSAMD21G18A-M | PA30 | SWCLK | Serial Wire Debug clock
ATSAMD21G18A-M | PA31 | SWDIO | Serial Wire Debug Data
ATSAMD21G18A-M | RESET | RESET | Microcontroller reset
ATSAMD21G18A-M | PB02 | IO_3 | General purpose input/output connected to button
ATSAMD21G18A-M | PB03 | RXLED | TX led
ATSAMD21G18A-M | PB08 | ADR_LED5 | Addressable led channel 5
ATSAMD21G18A-M | PB09 | ADR_LED6 | Addressable led channel 6
ATSAMD21G18A-M | PB10 | IO_4 | General purpose input/output pin FFC connector
ATSAMD21G18A-M | PB11 | IO_5 | General purpose input/output pin FFC connector
ATSAMD21G18A-M | PB22 | IO_6 | General purpose input/output pin FFC connector
ATSAMD21G18A-M | PB23 | IO_7 | General purpose input/output pin FFC connector

## Bibliography

Adafruit. (2023). Downloads. Retrieved from learn.adafruit: https://learn.adafruit.com/adafruitfeather-m0-express-designed-for-circuit-python-circuitpython/downloads

Atmel. (2023). Atmel start. Retrieved from strart.atmel: https://start.atmel.com/

Cypress. (2023). S25FL116K/S25FL132K/S25FL164. Retrieved from infineon: https://www.infineon.com/dgdl/Infineon-S25FL116K_S25FL132K_S25FL164K_16_MBIT_(2_MBYTE)_32_MBIT_(4_MBYTE)_64_MBIT_(8 _MBYTE)_3.0_V_SPI_FLASH_MEMORY-DataSheet-v10_00-EN.pdf?fileId=8ac78c8c7d0d8da4017d0ed4ebee537f

DigiKey. (2023). 2686. Retrieved from digikey: https://www.digikey.nl/en/products/detail/adafruitindustries-llc/2686/5804107?s=N4IgTCBcDaIMoGkBsAOAjGAsgSQHLZAF0BfIA

DigiKey. (2023). AT42QT2120-MMHR. Retrieved from digikey: https://www.digikey.nl/en/products/detail/microchip-technology/AT42QT2120-MMHR/3678702

DigiKey. (2023). MPR121QR2. Retrieved from digikey: https://www.digikey.nl/nl/products/detail/nxpusa-inc/MPR121QR2/2186527

Distrelec. (2023). ILPL-K5001-RGBW-SK105-01. Retrieved from distrelec: https://www.distrelec.be/nl/smd-led-5050-rgbw-460nm-505nm-615nm-intelligent-ledsolutions-ilpl-k501-rgbw-sk105-01/p/30308082

Distrelec. (2023). RND 135-00252. Retrieved from distrelec: https://www.distrelec.nl/nl/smd-led-rgbplcc-468-nm-520-nm-632-nm-rnd-components-rnd-135-00252/p/30158847?cq_src=google_ads&cq_cmp=18200849884&cq_con=&cq_term=&cq_med=pla&cq_plac=&cq_net=x&cq_pos=&cq_plt=gp&gclid=CjwKCAjwo9unBhBTEiwAipC118qLK gWXeMIWCFFvFx

Microchip. (2023). Low-Power, 32-bit Cortex-M0+ MCU with Advanced Analog. Retrieved from microchip:
https://ww1.microchip.com/downloads/aemDocuments/documents/MCU32/ProductDocuments/DataSheets/SAM-D21-DA1-Family-Data-Sheet-DS40001882H.pdf

Mouser. (2023). 19-337/R6GHBHC-A01/2T . Retrieved from mouser: https://nl.mouser.com/ProductDetail/Everlight/19-337-R6GHBHC-A01-2T?qs=8cKuZ6Ok2lbHoW%2FFyZa1pA%3D%3D

Mouser. (2023). AT25QL641-UUE-T . Retrieved from mouser: https://nl.mouser.com/ProductDetail/Renesas-Dialog/AT25QL641-UUE-T?qs=IS%252B4QmGtzzpVKdwhx%252BU4oA%3D%3D

Mouser. (2023). ATSAMD21G18A-AU. Retrieved from mouser: https://nl.mouser.com/ProductDetail/Microchip-Technology/ATSAMD21G18A-AU?qs=KLFHFgXTQiDh1vL0VLU76Q%3D%3D

Mouser. (2023). ATSAMD21G18A-MU. Retrieved from mouser: https://nl.mouser.com/ProductDetail/Microchip-Technology/ATSAMD21G18A-MU?qs=KLFHFgXTQiA%2FfMu%2FGM5u1A%3D%3D

Mouser. (2023). ATSAMD21J18A-AU. Retrieved from mouser: https://nl.mouser.com/ProductDetail/Microchip-Technology/ATSAMD21J18A-AU?qs=KLFHFgXTQiBwjHCNgKVs9A%3D%3D

Mouser. (2023). ATSAMD21J18A-CU. Retrieved from mouser: https://nl.mouser.com/ProductDetail/Microchip-Technology/ATSAMD21J18A-CU?qs=9KdFJXLqUo8%252BXJ5Hms4agg%3D%3D

Mouser. (2023). ATSAMD21J18A-MU. Retrieved from mouser: https://nl.mouser.com/ProductDetail/Microchip-Technology/ATSAMD21J18A-MU?qs=KLFHFgXTQiA5nYxZpqmjnQ%3D%3D

Mouser. (2023). CLQ6B-TKW-S1L1R1H1TBB7935CC3. Retrieved from mouser: https://nl.mouser.com/ProductDetail/Cree-LED/CLQ6B-TKW-S1L1R1H1TBB7935CC3?qs=Rp5uXu7WBW8kseQbCcO3Lg%3D%3D

Mouser. (2023). IN-P55QDTRGBW. Retrieved from mouser: https://nl.mouser.com/ProductDetail/Inolux/IN-P55QDTRGBW?qs=stqOd1AaK78tLn2kfF8cBA%3D%3D

Mouser. (2023). IS25LP032D-JLLE. Retrieved from mouser: https://nl.mouser.com/ProductDetail/ISSI/IS25LP032D-JLLE?qs=DXv0QSHKF4wnam7hnzWEbg%3D%3D

Mouser. (2023). IS25LP040E-JYLE-TR . Retrieved from mouser: https://nl.mouser.com/ProductDetail/ISSI/IS25LP040E-JYLE-TR?qs=eP2BKZSCXI5j9mdUcQ6FYg%3D%3D

Mouser. (2023). IS25LP064A-JLLE. Retrieved from mouser: https://nl.mouser.com/ProductDetail/ISSI/IS25LP064A-JLLE?qs=ULk7ZlyDR4f8APOHOBVPpg%3D%3D

Mouser. (2023). IS25LP064D-JBLA3. Retrieved from mouser: https://nl.mouser.com/ProductDetail/ISSI/IS25LP064D-JBLA3?qs=uwxL4vQweFM2ST8t4VRbqQ%3D%3D

Mouser. (2023). IS25LP064D-JKLE . Retrieved from mouser: https://nl.mouser.com/ProductDetail/ISSI/IS25LP064D-JKLE?qs=xZ%2FP%252Ba9zWqaUbrcT%2FGTrkA%3D%3D

Mouser. (2023). IS25LP080D-JULE-TR. Retrieved from mouser: https://nl.mouser.com/ProductDetail/ISSI/IS25LP080D-JULE-TR?qs=%252BEew9%252B0nqrBxcCxQG%252BlQOg%3D%3D

Mouser. (2023). IS25WP032D-JKLE. Retrieved from mouser: https://nl.mouser.com/ProductDetail/ISSI/IS25WP032D-JKLE?qs=DXv0QSHKF4zsRyVNAdaZLg%3D%3D

Mouser. (2023). IS25WQ040-JNLE. Retrieved from mouser: https://nl.mouser.com/ProductDetail/ISSI/IS25WQ040-JNLE?qs=TO8kDJPmCBRusxfzIU0lYg%3D%3D

Mouser. (2023). PCA8574D,518. Retrieved from mouser: https://nl.mouser.com/ProductDetail/NXP-Semiconductors/PCA8574D518?qs=LOCUfHb8d9tI6M3Msz5kkw%3D%3D

Mouser. (2023). PCA8575BS,118 . Retrieved from mouser: https://nl.mouser.com/ProductDetail/NXP-Semiconductors/PCA8575BS118?qs=LOCUfHb8d9uphqANyNY67Q%3D%3D

Mouser. (2023). PCA9536DR. Retrieved from mouser: https://nl.mouser.com/ProductDetail/Texas-Instruments/PCA9536DR?qs=aEuGZpxfbxUrMrsVTt7%252BhA%3D%3D

Mouser. (2023). PCA9548ABS,118. Retrieved from mouser: https://nl.mouser.com/ProductDetail/NXP-Semiconductors/PCA9548ABS118?qs=LOCUfHb8d9uF0VYCksl9OA%3D%3D

Mouser. (2023). PCA9670BS,118. Retrieved from mouser: https://nl.mouser.com/ProductDetail/NXP-Semiconductors/PCA9670BS118?qs=LOCUfHb8d9vyec%2F1PtVhAw%3D%3D

Mouser. (2023). PCA9685BS,118. Retrieved from mouser: https://nl.mouser.com/ProductDetail/NXP-Semiconductors/PCA9685BS118?qs=beN0Cyoe8Yle51zseU5uxw%3D%3D

Mouser. (2023). PCAL9722HNMP. Retrieved from mouser: https://nl.mouser.com/ProductDetail/NXP-Semiconductors/PCAL9722HNMP?qs=ulEaXIWI0c%2F4GQ1orHpXww%3D%3D

Mouser. (2023). SC-32S. Retrieved from mouser: https://nl.mouser.com/datasheet/2/360/file_PRODUCT_MASTER_50812_GRAPHIC03-542305.pdf

Mouser. (2023). SK6812MINI. Retrieved from mosuer: https://www.mouser.com/datasheet/2/737/SK6812MINI_REV_01_1_2-1915201.pdf

Mouser. (2023). SMD-LX0707RGB-TR . Retrieved from mouser: https://nl.mouser.com/ProductDetail/Lumex/SMD-LX0707RGB-TR?qs=u16ybLDytRYfAsx%252BT62puQ%3D%3D

Mouser. (2023). SMLP34RGBN1W3. Retrieved from mouser: https://nl.mouser.com/ProductDetail/ROHM-Semiconductor/SMLP34RGBN1W3?qs=Wj%2FVkw3K%252BMB6e39pO3qaCw%3D%3D

Mouser. (2023). SN74AHCT125DR. Retrieved from mouser: https://nl.mouser.com/ProductDetail/Texas-Instruments/SN74AHCT125DR?qs=B7lSdIxWQkm9VQkJOjfRaA%3D%3D

Mouser. (2023). SN74AHCT125RGYR. Retrieved from mouser: https://nl.mouser.com/ProductDetail/Texas-Instruments/SN74AHCT125RGYR?qs=WzgTT80quPG58uovxcQWdQ%3D%3D

Mouser. (2023). TL3342F260QG. Retrieved from mouser: https://nl.mouser.com/ProductDetail/E-Switch/TL3342F260QG?qs=6C6BR4UgC3Of90YOH%2FEXyw%3D%3D&mgh=1&gclid=CjwKCAjwo9unBhBTEiwAipC11_SAAIPyCmNt-0Y2xMbigZ8T0VGch7C7V15uZdR1J16C5-VcodVioBoC14IQAvD_BwE

Mouser. (2023). TLC59401RHBR. Retrieved from mouser: https://nl.mouser.com/ProductDetail/Texas-Instruments/TLC59401RHBR?qs=%2Fqzd9s%252BcLd5jLWxG9iB8xw%3D%3D

Mouser. (2023). TLC5940RHBR. Retrieved from mouser: https://nl.mouser.com/ProductDetail/Texas-Instruments/TLC5940RHBR?qs=p6lVfQR1GSql0QiKiHXw6g%3D%3D

Mouser. (2023). TLC5947RHBR. Retrieved from mouser: https://nl.mouser.com/ProductDetail/Texas-Instruments/TLC5947RHBR?qs=XGzIaZb%2FFYKg0KxHbVWJ0A%3D%3D

Mouser. (2023). TLC59711PWPR. Retrieved from mouser: https://nl.mouser.com/ProductDetail/Texas-Instruments/TLC59711PWPR?qs=0gJBXdIUCJmwn8liNLSqqA%3D%3D

Mouser. (2023). TS17-48-05-YE-260-SMT-TR. Retrieved from mouser: https://nl.mouser.com/ProductDetail/CUI-Devices/TS17-48-05-YE-260-SMT-TR?qs=tlsG%2FOw5FFgMrmlTrPhqZw%3D%3D

OpenAI. (2023). ChatGPT. Retrieved from chat.openai: https://chat.openai.com/

Reichelt. (2023). WUE 150141M1731. Retrieved from reichelt: https://www.reichelt.nl/nl/nl/rgb-ledsmd-3528-rood-groen-blauw-270-950-230-mcd-120--wue-150141m1731-p232068.html?PROVID=2809&gclid=CjwKCAjwo9unBhBTEiwAipC117XO2lOvVa-Djn6QAyeZty87x3jeCeQMU89jCTVnrXIqnveYX9ChUxoCqtcQAvD_BwE

TME. (2023). KAA-3528RGBS-11. Retrieved from tme: https://www.tme.eu/nl/details/kaa-3528rgbs-11/led-diodes-smd-gekleurd/kingbrightelectronic/?brutto=1&currency=EUR&gclid=CjwKCAjwo9unBhBTEiwAipC113EiGMlFlGeXmuBZfEKRWcfQH-Kf50QJdRfDlysYgNVbN9WMtGjeNRoC0iIQAvD_BwE

TME. (2023). WS2812B BLACK. Retrieved from tme: https://www.tme.eu/nl/details/ws2812b-b/leddiodes-smd-gekleurd/worldsemi/ws2812b-black/

Wright, L. (2023). PySpectrometerV2. Retrieved from github: https://github.com/leswright1977/PySpectrometer2

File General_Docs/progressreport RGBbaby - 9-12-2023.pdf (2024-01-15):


Class: | People of interest:
ESE-2A-n | Johan Korten,
| Paul van Wegen
Authors:
Joris Bol,
Emiel Visser
Version: | HAN_
V1.0 please don't print this document unless you really need to! | Arnhem, 9-12-2023

# PROGRESS REPORT RGBBABY

## Embedded Systems Engineering

1

## Index

Summary | 1
Introduction | 2
Goal | 2

This project aims to develop a system capable of dynamically altering the skin tone of a
reanimation doll | 2
Previous phase | 2
Current phase | 2
Activities and results | 2
Executed activities | 2
Obstacles | 2
Future | 2
To do | 2
Next period | 2
Conclusions and recommendations | 2

## Summary

This project aims to develop a system for dynamically changing a reanimation doll's skin tone. In the previous phase, a test circuit board was successfully produced but transitioned to Arduino due to time constraints and programming complexities. Challenges included finding suitable board files and libraries. The current phase focuses on the final printed circuit board using Arduino, with testing involving a 10x10cm silicone skin piece. Despite delays in programming, the project remains on track. Future tasks include ordering/soldering boards, software development, testing, and presenting findings to the product owner. The positive prognosis for the new board design and ongoing programming suggests confidence in the project's success in the final period. Emphasis on timely documentation updates is crucial.

2

## Introduction

### Goal

This project aims to develop a system capable of dynamically altering the skin tone of a reanimation doll.

### Previous phase

In the previous phase, we successfully produced a test circuit board and initially programmed it using embedded C. However, due to time constraints and the intricate nature of programming the microcontroller using embedded C, the decision was made to transition to Arduino, leveraging its extensive library support. However, we faced challenges in finding appropriate board files for the custom design and obtaining suitable libraries for the PWM LED driver and IO expander.

### Current phase

The focus of the current phase is to develop the final printed circuit board based on the findings from the test board. Arduino will be used for programming, and the completed program must be delivered by the end of this phase. Testing will involve a 10x10cm piece of skin made out of silicone. The results will be presented to the product owner, a nurse at WKZ.

## Activities and results

### Executed activities

We have conducted tests on the test board and created various test programs, leading to design choices for the new board. Despite taking more time than expected, the project remains on track.

### Obstacles

Despite taking more time than expected, the project remains on track. The programming aspect has proven to be challenging, especially with a microcontroller not natively supported by the Arduino IDE.

## Future

### To do

- Order the new printed circuit boards.
- Solder the boards.
- Develop software for the boards.
- Test the system with a 10x10cm piece of skin made out of silicone.
- Present findings to the product owner, a nurse at the WKZ.
- Update documentation to align with the current project status.

### Next period

This is the final period.

## Conclusions and recommendations

The prognosis is positive, with the new board design ready for ordering, and programming already underway. We do not see a need for significant changes in our approach at this time. It is however, important that updating documentation is crucial to keep it current with the project's progress. Overall, the team remains confident in the project's trajectory.

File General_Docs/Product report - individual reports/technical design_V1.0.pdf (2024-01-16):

# Technical design

By Manon Sijben, Marlon Reijlink, Emiel Visser and Joris Bol

DOCUMENT ORGANIZATIONAL DETAILS:
Document Type:
Skills Consultant: | Paul van Wegen
Project Client: | Johan Korten
Education: | Embedded Systems Engineering
Institute: | School of Engineering and Automotive, Hogeschool Arnhem-Nijmegen
Report Date: | 16-1-2024
Report Version: | v1.0
Project Duration:
Education Term:
Students: | 2108100 (Joris Bol), 2111740(Emiel Visser), 2106573 (Manon Sijben),
| 2107003 (Marlon Reijlink)

Embedded Systems Engineering · HAN University of Applied Sciences

## Version management

Version: | Date: | Change: | Name:
V1.0 | 5-9-2023 | Creation document. | J. Bol
V1.0 | 17-9-2023 | Added paragraphs. | E. Visser
V1.0 | 16-10-2023 | Added info. | E. Visser
V1.0 | 27-11-2023 | Added info. | E. Visser
V1.0 | 1-12-2023 | Added info. | E. Visser
V1.0 | 9-12-2023 | Added info. | E. Visser
V1.0 | 10-12-2023 | Added info. | E. Visser
V1.0 | 18-12-2023 | Added info. | J. Bol
V1.0 | 16-1-2023 | Spellcheck. | E. Visser

## Table of contents

## 1 – Technical design

About the exact reason why we choose these sensors and actuators we would like to point you to our preliminary research.

### 4.1- Architecture

In figure 1 a diagram is shown showing how our system will be controlled. The boxes contain one or more items which the board will interface with. The arrows between the boxes and board indicate the direction of the data/energy flow. The protocol/voltage is placed on the arrow.


Figure 1: system interconnections

### 4.2 – Interfaces

In this paragraph all of the interfaces between the board and the items are described. An overview of the interfaces and items can be seen in figure 1.

4.2.1 – Power
In this paragraph the power section of our system will be described.

4.2.1.1 – USB-C
To deliver power and upload code to our board we have added a UCB type C port to our PCB. We have added two test points so that the USB protocol can be debugged if necessary. The USB termination resistors are placed in the main sheet and are there to reduce ringing on the USB data lines. An ESD protection diode protects the host (e.g. a laptop) from ESD. The USB C port can deliver a maximum of 3A in this configuration.

Note: Don’t come close to this maximum though because the traces coming out of the port might not be able to handle 3A!

Requirement supports T7:

Specification 1.1:

No software scheme for mounting holes and fiducials.


Specification 1.2:

4.1.1.2 – Auxiliary power
A USB C plug can be quite bulky, so we decided to add another way of powering the system. That’s way we added a JST-XH port where 5V power can be fed into the system. We also added a fuse holder. We recommend using a fast blow fuse to protect the system in an overcurrent event.

Note: The maximum current for prolonged periods is about 2.5A. For short periods 3A is possible.

Requirement supports T7:

Specification 2.1:

No software scheme for aforementioned element.

Specification 2.2:


4.1.1.3 – 3.3V regulator
We have decided top go with an AP2112K type regulator. This regulator drops the auxiliary and/or USB voltage down to 3.3V which is used by the microcontroller and other components. The regulator is decoupled using three decoupling capacitors and will deliver 3.3V when 5V is applied to its input.

Requirement supports T7:

Specification 3.1:

No software scheme for aforementioned element.


Specification 3.2:

4.2.2 – Status leds
We have integrated multiple leds onto the board to provide users with clear visual indicators for various processes taking place on the controller board. These leds serve as a user-friendly interface, offering real-time feedback on the ongoing activities and status of the system.

4.2.2.1 – Status led (neopixel)
We have opted for the SK6812MINI Neopixel led due to its compact package size. Additionally, these leds offer significant IO savings, a crucial factor because we decided to go with the ATSAMD21G18 instead of the original ATSAMD21J18 microcontroller. Another compelling reason for choosing this specific led is its compatibility with the existing protocol we are using for other leds. This not only streamlines our development process but also minimizes the need for additional code, promoting efficiency and consistency across our lighting system.

Requirement: supports T10


Specification 4.1:


Specification 4.2:

4.2.2.2 – HB led (heartbeat)
The Heartbeat led blinks at a fixed frequency. In the event that this led stops blinking, it indicates a system crash or that the system is stuck in a loop. Typically, a system reset is the recommended solution to address such issues.

Requirement supports T10

Specification 5.1:

Specification 5.2:

4.2.2.3 – Health led
This led will be on when the board is in good health. And will turn of when the board encounters errors that it can’t handle properly.

Requirement supports T10


Specification 6.1:

Specification 6.2:

4.2.2.4 – Voltage indicator leds
We've added voltage indicator leds on the board for a quick check on the availability of the two supply voltages.

Requirement supports T10

Specification 7.1:

No software scheme for aforementioned element.

Specification 7.2:


4.2.2.5 – Receive and transmit leds
To give the user an indication if the serial bus is working, we have added a TX and RX led.

Requirement T10

Specification 8.1:

No software scheme for aforementioned element.

Specification 8.2

4.2.3 – Main leds
We have found that the SMD-LX0707RGB-TR leds fit our requirements.

Requirement T5.3


Specification 9.1:

Specification 9.2

4.2.3.1- Neopixel output drivers
To convert the 3.3V microcontroller output signal to a 5V output signal which results in a more stable signal. We have chosen the SN74AHCT125RGYR buffer IC. In our tests we have used the SN74AHCT125DR. the RGYR version has a smaller package which is why we went with this version for our latest revision. Every in- and output has a test point.

Requirement supports T5.3.

Specification 10.1:

No software scheme for aforementioned element.


Specification 10.2:

4.2.3.2 – FFC/FPC flat cable connectors
To connect the flex PCBs to our control PCB we are using 16pin FFC/FPC connectors. We are using 1A resettable fuses on the 5V and 3.3V power rails. The 62-ohm resistors are there to prevent ringing on the data lines. We have also opted to breakout an I2C bus to pin 11 and 12 on the connector which enables a next group to add a I2C enabled device to be used on the flex PCBs. We also decided to breakout two IO’s to pin 8 and 9 on the connector. The user can use the for general purpose applications.

Note: The connector only makes contact on the under side so if you want your parts to be on top of the flexible PCB you need to place the connector on the underside!

Requirement T5

Specification 11.1:

No software scheme for aforementioned element.


Specification 11.2:

4.2.4 – Microcontroller
We have chosen the ATSAMD21G18A microcontroller. This microcontroller is used by the Adafruit feather M0 express board which makes integration with Arduino or some other platform a lot easier.

Requirement T1

Specification 12.1:

The software for the microcontroller is the combination of the other specified software schematics.

Specification 12.2:

Note: The decoupling capacitors and filtering for the MCU can be found in the Power sheet of the schematic.


3

4.2.4.1 – Clock
The SAMD21G18A runs on a 32.768mHz clock crystal. C1 and C2 are load capacitors. These are crucial for getting the correct clock speed. If you end up going with a different clock crystal, you will need te recalculate the load capacitors. The formula is in the schematic. But this formula is incorrect. You can verify the clock speed at the test points we have placed on the clock pins.

Requirement supports T1

Specification 13.1:

No software scheme for aforementioned element.

Specification 13.2:


4.2.4.2 – Flash memory
We are using a 32kb flash chip. The chip communicates via SPI. Every communication pin has been connected to a test point making debugging easier.

Requirement general functionality


Specification 14.1:

Specification 14.2:


4.2.4.3 – Debug header
If you want to write software to the chip (e.g. flashing a bootloader) you can use this port with a programmer like the J-LINK mini edu. This port can also be used to debug the processor and peripherals. We have added test points on the reset and data lines just in case.

Requirement general functionality

Specification 15.1:

No software functions for debug header.

Specification 15.2:


4.2.4.3 – Reset button
To reset the system, we can use the physical reset button.

Requirement general functionality

Specification 16.1:

No software schemes for reset button.

Specification 16.2:

4.2.5 – User button
We had one IO left so we routed that to a button. This button also has a test point.

Requirement general functionality


Specification 17.1:

Specification 17.2:


4.2.6 – I2C bus components
There are three I2C busses available. All I2C busses have test points.

4.2.6.1 – Main bus
The main bus is the communication bus that communicates with other modules in the baby doll. The main bus has two ports. Main bus in and main bus out. You should connect the output cable of the previous module to the main bus in port on the PCB INT4 is connected to main bus in. The main bus out port connects to the next module. INT5 is connected to this port.

Requirement T7


Specification 18.1:

Specification 18.2:

4.2.6.2 – IO bus


We wanted to maintain the possibility to add other I2C enabled devices to the flex PCBs. This is why we have broken out one I2C bus to every FFC/FPC connector. This bus also has test points.

Requirement supports T6

Specification 19.1:

See specification 18.1.

Specification 19.2:
Note: I2C output pins can be found in paragraph 4.2.3.2 – FFC/FPC flat cable connectors


4.2.6.3 – Auxiliary bus
This bus is meant for auxiliary sensors. This bus does not have an interrupt pin connected to it and the output voltage is 3.3V only. We have used a JST-XH connector. We also added more test points tot the data pins.

Requirement supports T6

Specification 20.1:

See specification 18.1.


Specification 20.2:


4.2.7 – Mounting holes and fiducials
We have added mounting holes to the PCB the hole size is 3.2mm which means a M3 screw can be used to secure the PCB into place. The exposed copper pads near the screw hole are not connected to ground. The fiducials are positioning marks for the PCB manufacturer and pick-and-place machine.

Requirement general functionality

Specification 21.1:
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

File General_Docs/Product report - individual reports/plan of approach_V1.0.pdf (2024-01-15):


# Plan of Approach - BabySim


Authors: | Emiel Visser, Manon Sijben, Marlon Reijlink, Joris Bol.
Supervisor: | Johan Korten.
Last change: | 2-10-2023.
Version: | V1.0

## Version:

Version: | Change: | Date: | Name:
V1.0 | Initial document version | 29-8-2023 | Joris
V1.0 | Added information | 31-8-2023 | Emiel
V1.0 | Added information | 2-9-2023 | Emiel
V1.0 | Added Gannt diagram | 4-9-2023 | Joris
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

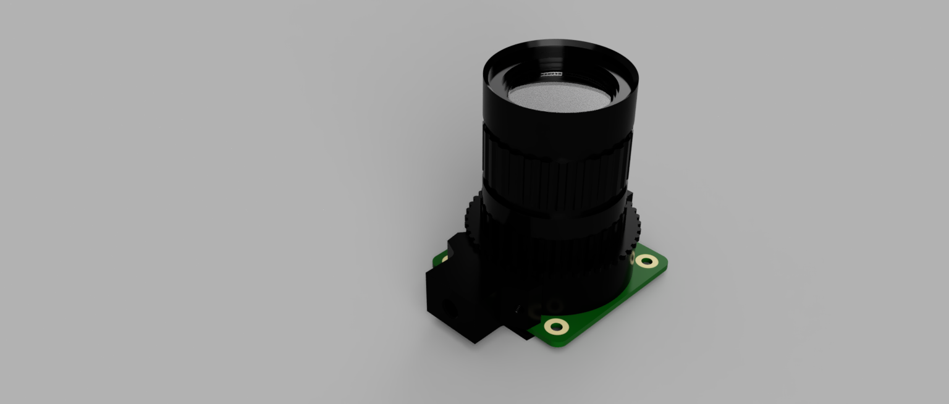
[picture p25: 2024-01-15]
Pi_Spectrometer/Cad/raspberry-pi-hq-camera-with-arducam-cs-mount-lens-1.snapshot.3/Raspberry_Pi_HQ_Camera_with_cs_mount_lens_2022-Apr-17_11-12-33AM-000_CustomizedView1210793441.png

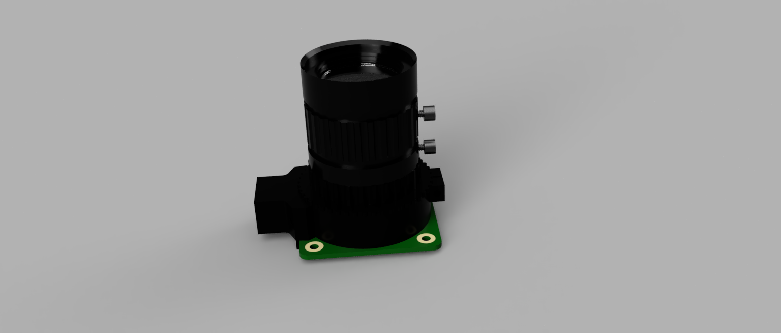
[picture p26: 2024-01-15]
Pi_Spectrometer/Cad/raspberry-pi-hq-camera-with-arducam-cs-mount-lens-1.snapshot.3/86030140-17f2-427e-8b92-9298e140210a.PNG

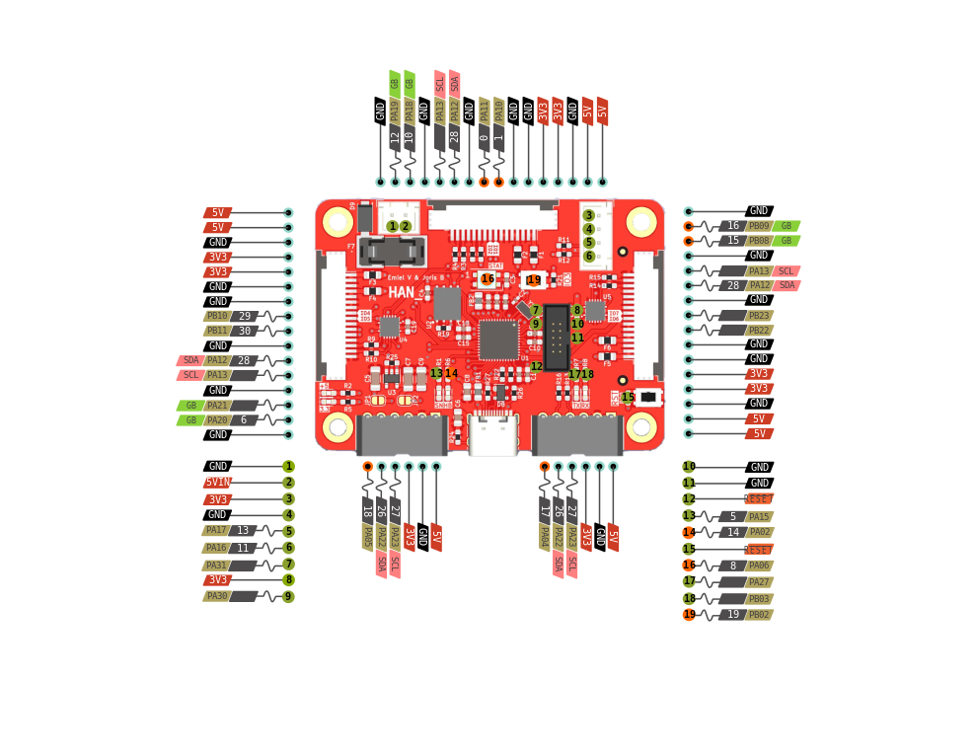
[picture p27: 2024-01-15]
PCBs/LedDriverBoardV3/Pcb/Docs/driverBoardInfo.png

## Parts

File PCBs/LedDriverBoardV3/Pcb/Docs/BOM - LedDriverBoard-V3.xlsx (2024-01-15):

Catagory | Name in schematic: | Name/Value | Mounting type | Footprint: | Nr. per. PCB: | Amount of PCBs: | Total amount: | To order: | Price per.part: | Price total: | Link:
FLASH | U2 | IS25LP032D-JLLE | SMD | SON127P600X500X75-9N-D | 1 | 2 | 2 | 3 | €0.83 | €2.48 | https://nl.mouser.com/ProductDetail/ISSI/IS25LP032D-JKLE-TR?qs=DXv0QSHKF4y2R7%2F4oqToPQ%3D%3D
CONNECTOR | J5, J6 | 1778667 | THT | SHDRRA6W70P0X250_1X6_1670X750X510P | 2 | 2 | 4 | 5 | €1.43 | €7.15 | https://nl.mouser.com/ProductDetail/Phoenix-Contact/1778667?qs=i0qWf6NAoDtdrKZdTiVKlQ%3D%3D
GATEBUFFER | U4, U5 | SN74AHCT125RGYR | SMD | RGY-_S-PVQFN-N14_ | 2 | 2 | 4 | 4 | €0.44 | €1.75 | https://nl.mouser.com/ProductDetail/Texas-Instruments/SN74AHCT125RGYR?qs=WzgTT80quPG58uovxcQWdQ%3D%3D
RESISTOR | R5, R7 | 470 | SMD | 0603 | 2 | 2 | 4 | 10 | €0.01 | €0.10 | https://nl.mouser.com/ProductDetail/YAGEO/RC0603FR-10470RL?qs=EiqXWrxQq62gi8HBTlzDog%3D%3D
CAPACITOR | C4, C12, C14, C15, C16, C19, C20 | 100nF | SMD | 0603 | 7 | 2 | 14 | 20 | €0.03 | €0.50 | https://nl.mouser.com/ProductDetail/KYOCERA-AVX/06035C104KAT2A?qs=wORnlwVG%2F0dQ8Y%2FnMEnCGg%3D%3D
RESISTOR | R2 | 2.2k | SMD | 0603 | 1 | 2 | 2 | 10 | €0.09 | €0.93 | https://nl.mouser.com/ProductDetail/SEI-Stackpole/RMCF0603FT2K20?qs=FESYatJ8odLT3Yuphfww0w%3D%3D
RESISTOR | R19, R20, R21 | 10k | SMD | 0603 | 3 | 2 | 6 | 10 | €0.02 | €0.16 | https://nl.mouser.com/ProductDetail/Bourns/CR0603AFX-1002EAS?qs=PzGy0jfpSMvnIWl2FjD7DQ%3D%3D
CONNECTOR | J1, J2, J3 | Conn_01x16_Pin | SMD | TE_1-84952-6_1x16-1MP_P1.0mm_Horizontal | 3 | 2 | 6 | 10 | €0.87 | €8.74 | https://nl.mouser.com/ProductDetail/TE-Connectivity/1-84952-6?qs=uUkeXfjQ8uRn%252Bu4rrhD4JA%3D%3D
RESISTOR | C5, C7 | 10uF | SMD | 1206 | 2 | 2 | 4 | 10 | €0.34 | €3.35 | https://nl.mouser.com/ProductDetail/KEMET/C1206C106K4RACTU?qs=guDyKOyRtV0mxqxQedB7kA%3D%3D
RESISTOR | R3, R4, R9, R10, R14, R15 | 62 | SMD | 0603 | 6 | 2 | 12 | 20 | €0.02 | €0.20 | https://nl.mouser.com/ProductDetail/YAGEO/RE0603FRE0762RL?qs=fTsMJN6MUUv1sp9RVyQSKw%3D%3D
CAPACITOR | C6 | 4.7nF 1kV | SMD | 0805 | 1 | 2 | 2 | 10 | €0.19 | €1.94 | https://nl.mouser.com/ProductDetail/Walsin/0805B472K102CT?qs=hzBznG4dWXXfDjU4OfxUFQ%3D%3D
CAPACITOR | C10, C13, C17, C18 | 10uF | SMD | 0603 | 4 | 2 | 8 | 10 | €0.10 | €0.96 | https://nl.mouser.com/ProductDetail/Murata-Electronics/GRM188C81C106MA73D?qs=W1gvEE3epjzPVR28V3qh%2Fw%3D%3D
LED | D3, D5 | GREEN | SMD | 0603 | 2 | 2 | 4 | 10 | €0.21 | €2.14 | https://nl.mouser.com/ProductDetail/Lite-On/LTST-C171GKT?qs=DXsB9OwW3bmgO%252BU8es%2F20A%3D%3D
RESISTOR | R1, R6, R8 | 330 | SMD | 0603 | 3 | 2 | 6 | 10 | €0.01 | €0.08 | https://nl.mouser.com/ProductDetail/SEI-Stackpole/RMCF0603FT330R?qs=FESYatJ8odLaN56qufdyJQ%3D%3D
RESISTOR | R22, R23 | 27 | SMD | 0603 | 2 | 2 | 4 | 10 | €0.03 | €0.26 | https://nl.mouser.com/ProductDetail/TE-Connectivity-Holsworthy/CRG0603F27R?qs=VHcS2MTj4gbfJ48omZvbHQ%3D%3D
FUSE | F1, F2, F3, F4, F5, F6 | 1A | SMD | 0805 | 6 | 2 | 12 | 20 | €0.19 | €3.86 | https://nl.mouser.com/ProductDetail/Bel-Fuse/0ZCK0050FF2E?qs=SRYZG9HaIQ3gw527qS%252BJNw%3D%3D
CRYSTAL | Y1 | 32.768mHz | SMD | Crystal_SMD_3215-2Pin_3.2x1.5mm | 1 | 2 | 2 | 4 | €0.38 | €1.53 | https://nl.mouser.com/ProductDetail/Seiko-Semiconductors/SC32S-7PF20PPM?qs=3CPZD7qAgigZSR1ASVAS6w%3D%3D
DIODE | D9 | SS34ALH | SMD | SMA | 1 | 2 | 2 | 4 | €0.48 | €1.94 | https://nl.mouser.com/ProductDetail/Taiwan-Semiconductor/SS34ALH?qs=A6eO%252BMLsxmQip%2FrgNup6RA%3D%3D
LED | D1 | BLUE | SMD | 0603 | 1 | 2 | 2 | 3 | €0.29 | €0.86 | https://nl.mouser.com/ProductDetail/Lite-On/LTST-C171TBKT?qs=DIGZ1Yxiz2%2FRYShBNqRoMg%3D%3D
LED | D2, D4 | RED | SMD | 0603 | 2 | 2 | 4 | 3 | €0.25 | €0.75 | https://nl.mouser.com/ProductDetail/Lite-On/LTST-C171KRKT?qs=5XMAZBf2SiSTcAb1f5vDzw%3D%3D
FUSE | F7 | - | SMD | 0031.7701.11 | 1 | 2 | 2 | 3 | €1.29 | €3.87 | https://nl.mouser.com/ProductDetail/Schurter/0031.7701.11
FUSE | - | 3A | SMD | OMF 125 | 1 | 2 | 2 | 4 | €0.79 | €3.16 | https://nl.mouser.com/ProductDetail/Schurter/3404.0014.11?qs=8QfiMw8FY5MW%252BuaV2dEayA%3D%3D
CAPACITOR | C9 | 1uF | SMD | 1206 | 1 | 2 | 2 | 10 | €0.01 | €0.05 | https://nl.mouser.com/ProductDetail/Samsung-Electro-Mechanics/CL31B105KOFNNNE?qs=349EhDEZ59o%252Bj%2FvC1Fmg0w%3D%3D
CAPACITOR | C3, C11 | 1uF | SMD | 0603 | 2 | 2 | 4 | 10 | €0.02 | €0.21 | https://nl.mouser.com/ProductDetail/KYOCERA-AVX/KGM15AR71C104KT?qs=Jm2GQyTW%2FbiNMH1Ynxi4nA%3D%3D
RESISTOR | R11, R12, R13, R16, R17, R18 | 4.7k | SMD | 0603 | 6 | 2 | 12 | 20 | €0.06 | €1.22 | https://nl.mouser.com/ProductDetail/Welwyn-Components-TT-Electronics/WCR0603-4K7FI?qs=mbEfOQsdCzfBCmdhoNRGyQ%3D%3D
LDO | U3 | AP2112K-3.3 | SMD | SOT-23-5 | 1 | 2 | 2 | 4 | €0.33 | €1.30 | https://nl.mouser.com/ProductDetail/Diodes-Incorporated/AP2112K-3.3TRG1?qs=x6A8l6qLYDDPYHosCdzh%2FA%3D%3D
FERRITE | FB1,FB2 | FerriteBead | SMD | 0805 | 2 | 2 | 4 | 10 | €0.10 | €1.02 | https://nl.mouser.com/ProductDetail/TDK/MPZ2012S101AT000?qs=pLY5GE0xrmKpe1XYPmVCHA%3D%3D
RESISTOR | R24 | 1M | SMD | 0603 | 1 | 2 | 2 | 10 | €0.01 | €0.08 | https://nl.mouser.com/ProductDetail/SEI-Stackpole/RMCF0603FT1M00?qs=FESYatJ8odJNClY0wUC1cg%3D%3D
SWITCH | SW1,SW2 | PTS810SJK250SMTRLFS | SMD | SW_SPST_B3U-1000P | 2 | 2 | 4 | 5 | €0.32 | €1.58 | https://nl.mouser.com/ProductDetail/CK/PTS810SJK250SMTRLFS?qs=UxeAxwACbqlfHzoZSrW3%2Fw%3D%3D
USB | J8 | USB_C_Receptacle_USB2.0 | SMD | USB_C_Receptacle_HRO_TYPE-C-31-M-12 | 1 | 2 | 2 | 4 | €0.84 | €3.35 | https://nl.mouser.com/ProductDetail/Molex/217179-0001?qs=DRkmTr78QAQqCH4BoIR1xg%3D%3D
ESD | D8 | PRTR5V0U2X | SMD | SOT-143 | 1 | 2 | 2 | 4 | €0.05 | €0.19 | https://nl.mouser.com/ProductDetail/Nexperia/PRTR5V0U2X215?qs=LOCUfHb8d9sDkgY4cRj8Lw%3D%3D
PHY | U1 | ATSAMD21G18A-M | SMD | QFN-48-1EP_7x7mm_P0.5mm_EP5.15x5.15mm | 1 | 2 | 2 | 3 | €3.79 | €11.37 | https://nl.mouser.com/ProductDetail/Microchip-Technology/ATSAMD21G18A-MU?qs=KLFHFgXTQiA%2FfMu%2FGM5u1A%3D%3D
RESISTOR | R26, R27 | 5.1k 1% | SMD | 0603 | 2 | 2 | 4 | 10 | €0.01 | €0.15 | https://nl.mouser.com/ProductDetail/Bourns/CR0603AFX-5101EAS?qs=PzGy0jfpSMub%2Fi7zoEnwAw%3D%3D
CAPACITOR | C2,C1 | 15pF | SMD | 0402 | 2 | 2 | 4 | 10 | €0.17 | €1.70
CAPACITOR | C8 | 100uF | SMD | 0603 | 1 | 2 | 2 | 10 | €0.11 | €1.06 | https://nl.mouser.com/ProductDetail/KEMET/C0805C104K4RECAUTO?qs=MLItCLRbWswQcXlGMGaWig%3D%3D
LED | D6 | ORANGE | SMD | 0805 | 1 | 2 | 2 | 4 | €0.25 | €1.00 | https://nl.mouser.com/ProductDetail/Lite-On/LTST-C170KFKT?qs=gKd32bbgGM%2FWUWN9MKaKoA%3D%3D
RESISTOR | R25 | 100k | SMD | 0603 | 1 | 2 | 2 | 10 | €0.04 | €0.35 | https://nl.mouser.com/ProductDetail/Vishay-Draloric/RCG0603100KFKEA?qs=f%2F0S6rTelyXH%2FpVkET7riQ%3D%3D
NEOPIXEL | D10 | SK6812MINI | SMD | LED_SK6812MINI_PLCC4_3.5x3.5mm_P1.75mm | 1 | 2 | 2 | 4 | €0.27 | €1.10 | https://nl.mouser.com/ProductDetail/Adafruit/4960?qs=pBJMDPsKWf1Q%252BqeEoLnQjA%3D%3D
 |  |  |  |  |  |  | Amount of PCBs | €36.22 | Total: | €72.45

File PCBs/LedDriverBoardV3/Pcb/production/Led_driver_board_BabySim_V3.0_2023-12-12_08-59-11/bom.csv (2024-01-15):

Designator | Footprint | Quantity | Value | LCSC Part #
C1, C2 | 0402 | 2 | 15pF
C10, C13, C17, C18 | 0603 | 4 | 10uF
C11, C3 | 0603 | 2 | 1uF
C12, C14, C15, C16, C19, C20, C4 | 0603 | 7 | 100nF
C5, C7 | 1206 | 2 | 10uF
C6 | 0805 | 1 | 4.7nF 1kV
C8 | 0805 | 1 | 100uF
C9 | 1206 | 1 | 1uF
D1 | 0603 | 1 | BLUE
D10 | LED_SK6812MINI_PLCC4_3.5x3.5mm_P1.75mm | 1 | SK6812MINI
D2, D4 | 0603 | 2 | RED
D3, D5 | 0603 | 2 | GREEN
D6 | 0603 | 1 | ORANGE
D8 | SOT-143 | 1 | PRTR5V0U2X
D9 | DIOM5127X229N | 1 | D_Schottky
F1, F2, F3, F4, F5, F6 | 0805 | 6 | Polyfuse
F7 | 0031.7701.11 | 1 | Fuse
FB1, FB2 | 0805 | 2 | FerriteBead
FID1, FID2, FID3 | Fiducial_1mm_Mask2mm | 3 | Fiducial
H1, H2, H3, H4 | MountingHole_3.2mm_M3_DIN965_Pad | 4 | MountingHole
J1, J2, J3 | TE_1-84952-6_1x16-1MP_P1.0mm_Horizontal | 3 | Conn_01x16_Pin
J4 | JST_XH_B4B-XH-A_1x04_P2.50mm_Vertical | 1 | Conn_01x04_Socket
J5, J6 | SHDRRA6W70P0X250_1X6_1670X750X510P | 2 | 1778667
J7 | PinSocket_2x05_P1.27mm_Vertical | 1 | Conn_02x05_Odd_Even
J8 | USB_C_Receptacle_HRO_TYPE-C-31-M-12 | 1 | USB_C_Receptacle_USB2.0
J9 | JST_XH_B2B-XH-A_1x02_P2.50mm_Vertical | 1 | Conn_01x02_Socket
JP1, JP2 | SolderJumper-2_P1.3mm_Open_RoundedPad1.0x1.5mm | 2 | Jumper_2_Open
R1, R6, R8 | 0603 | 3 | 330
R10, R14, R15, R3, R4, R9 | 0603 | 6 | 62
R11, R12, R13, R16, R17, R18 | 0603 | 6 | 4.7k
R19, R20, R21 | 0603 | 3 | 10k
R2 | 0603 | 1 | 2.2k
R22, R23 | 0603 | 2 | 27
R24 | 0603 | 1 | 1m
R25 | 0603 | 1 | 100k
R26, R27 | 0603 | 2 | 5.1k 1%
R5, R7 | 0603 | 2 | 470
SW1, SW2 | SW_SPST_PTS810 | 2 | SW_Push
TP1 | TestPoint_Pad_D1.5mm | 1 | IO_1
TP10 | TestPoint_Pad_D1.5mm | 1 | INT4
TP11 | TestPoint_Pad_D1.5mm | 1 | INT5
TP12 | TestPoint_Pad_D1.5mm | 1 | NEOPIXEL
TP13 | TestPoint_Pad_D1.5mm | 1 | SWD
TP14 | TestPoint_Pad_D1.5mm | 1 | CLK
TP15 | TestPoint_Pad_D1.5mm | 1 | SCL_SEN
TP16 | TestPoint_Pad_D1.5mm | 1 | SDA_SEN
TP17 | TestPoint_Pad_D1.5mm | 1 | RST
TP18 | TestPoint_Pad_D1.5mm | 1 | CS
TP19 | TestPoint_Pad_D1.5mm | 1 | SCK
TP2 | TestPoint_Pad_D1.5mm | 1 | IO_2
TP20 | TestPoint_Pad_D1.5mm | 1 | MOSI
TP21 | TestPoint_Pad_D1.5mm | 1 | MISO
TP22 | TestPoint_Pad_D1.5mm | 1 | SCL
TP23 | TestPoint_Pad_D1.5mm | 1 | SDA
TP24 | TestPoint_Pad_D1.5mm | 1 | SCL_IO
TP25 | TestPoint_Pad_D1.5mm | 1 | SDA_IO
TP26 | TestPoint_Pad_D1.5mm | 1 | 5V
TP27 | TestPoint_Pad_D1.5mm | 1 | 3.3V
TP28 | TestPoint_Pad_D1.5mm | 1 | D-
TP29 | TestPoint_Pad_D1.5mm | 1 | D+
TP3 | TestPoint_Pad_D1.5mm | 1 | IO_3
TP30 | TestPoint_Pad_D1.5mm | 1 | 5V_AUX
TP31 | TestPoint_Pad_D1.5mm | 1 | ADR_LED1
TP32 | TestPoint_Pad_D1.5mm | 1 | ADR_LED2
TP33 | TestPoint_Pad_D1.5mm | 1 | ADR_LED3
TP34 | TestPoint_Pad_D1.5mm | 1 | ADR_LED4
TP35 | TestPoint_Pad_D1.5mm | 1 | ADR_LED5
TP36 | TestPoint_Pad_D1.5mm | 1 | ADR_LED6
TP37 | TestPoint_Pad_D1.5mm | 1 | OUT_LED1
TP38 | TestPoint_Pad_D1.5mm | 1 | OUT_LED2
TP39 | TestPoint_Pad_D1.5mm | 1 | OUT_LED3
TP4 | TestPoint_Pad_D1.5mm | 1 | IO_4
TP40 | TestPoint_Pad_D1.5mm | 1 | OUT_LED4
TP41 | TestPoint_Pad_D1.5mm | 1 | OUT_LED5
TP42 | TestPoint_Pad_D1.5mm | 1 | OUT_LED6
TP5 | TestPoint_Pad_D1.5mm | 1 | IO_5
TP6 | TestPoint_Pad_D1.5mm | 1 | IO_6
TP7 | TestPoint_Pad_D1.5mm | 1 | IO_7
TP8 | TestPoint_Pad_D1.5mm | 1 | CLK_A1
TP9 | TestPoint_Pad_D1.5mm | 1 | CLK_A0
U1 | QFN-48-1EP_7x7mm_P0.5mm_EP5.15x5.15mm | 1 | ATSAMD21G18A-M
U2 | SON127P600X500X75-9N-D | 1 | IS25LP032D-JLLE
U3 | SOT-23-5 | 1 | AP2112K-3.3
U4, U5 | RGY-_S-PVQFN-N14_ | 2 | SN74AHCT125RGYR
Y1 | Crystal_SMD_3215-2Pin_3.2x1.5mm | 1 | 32.768mHz

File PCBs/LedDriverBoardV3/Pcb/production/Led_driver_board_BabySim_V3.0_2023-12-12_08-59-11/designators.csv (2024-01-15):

C1:1
C10:1
C11:1
C12:1
C13:1
C14:1
C15:1
C16:1
C17:1
C18:1
C19:1
C2:1
C20:1
C3:1
C4:1
C5:1
C6:1
C7:1
C8:1
C9:1
D1:1
D10:1
D2:1
D3:1
D4:1
D5:1
D6:1
D8:1
D9:1
F1:1
F2:1
F3:1
F4:1
F5:1
F6:1
F7:1
FB1:1
FB2:1
FID1:1
FID2:1
FID3:1
G***:1
H1:1
H2:1
H3:1
H4:1
J1:1
J2:1
J3:1
J4:1
J5:1
J6:1
J7:1
J8:1
J9:1
JP1:1
JP2:1
R1:1
R10:1
R11:1
R12:1
R13:1
R14:1
R15:1
R16:1
R17:1
R18:1
R19:1
R2:1
R20:1
R21:1
R22:1
R23:1
R24:1
R25:1
R26:1
R27:1
R3:1
R4:1
R5:1
R6:1
R7:1
R8:1
R9:1
REF**:2
SW1:1
SW2:1
TP1:1
TP10:1
TP11:1
TP12:1
TP13:1
TP14:1
TP15:1
TP16:1
TP17:1
TP18:1
TP19:1
TP2:1
TP20:1
TP21:1
TP22:1
TP23:1
TP24:1
TP25:1
TP26:1
TP27:1
TP28:1
TP29:1
TP3:1
TP30:1
TP31:1
TP32:1
TP33:1
TP34:1
TP35:1
TP36:1
TP37:1
TP38:1
TP39:1
TP4:1
TP40:1
TP41:1
TP42:1
TP5:1
TP6:1
TP7:1
TP8:1
TP9:1
U1:1
U2:1
U3:1
U4:1
U5:1
Y1:1
kibuzzard-6574499F:1
kibuzzard-657449AF:1
kibuzzard-65744A4B:2
kibuzzard-65744A5E:2
kibuzzard-65744A66:2
kibuzzard-65744A78:2
kibuzzard-65744A88:2
kibuzzard-65744B8B:1
kibuzzard-65744BA2:1
kibuzzard-65744BAF:1
kibuzzard-65744BC6:1
kibuzzard-65744BCE:1
kibuzzard-65744F40:1
kibuzzard-65744F4B:1
kibuzzard-65744FA3:1
kibuzzard-65744FAF:1
kibuzzard-6574640D:1
kibuzzard-6574D547:1
kibuzzard-6574D579:1
kibuzzard-6574D62C:1
kibuzzard-6574D710:1
kibuzzard-6574D849:1
kibuzzard-6574DAA4:1
kibuzzard-6574DAAD:1

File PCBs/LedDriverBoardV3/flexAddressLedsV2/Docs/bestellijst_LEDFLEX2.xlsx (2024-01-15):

Catagory | Name in schematic: | Name/Value | Mounting type | Footprint: | Nr. per. PCB: | Amount of PCBs: | Total amount: | To order: | Price per.part: | Price total: | Link:
LED | IC1, IC2, IC3, IC4, IC5, IC6, IC7, IC8, IC9, IC10, IC11, IC12, IC13, IC14, IC15, IC16, IC17, IC18, IC19, IC20, IC21, IC22, IC23, IC24, IC25, IC26, IC27, IC28, IC29, IC30, IC31, IC32, IC33, IC34, IC35, IC36, IC37, IC38, IC39, IC40, IC41, IC42, IC43, IC44, IC45, IC46, IC47, IC48, IC49, IC50, IC51, IC52, IC53, IC54, IC55, IC56, IC57, IC58, IC59, IC60, IC61, IC62, IC63, IC64, IC65, IC66, IC67, IC68, IC69, IC70, IC71, IC72, IC73, IC74, IC75, IC76, IC77, IC78, IC79, IC80, IC81, IC82, IC83, IC84, IC85, IC86, IC87, IC88, IC89, IC90, IC91, IC92, IC93, IC94, IC95, IC96, IC97, IC98, IC99, IC100, IC101, IC102, IC103, IC104, IC105, IC106, IC107, IC108, IC109, IC110, IC111, IC112, IC113, IC114, IC115, IC116, IC117, IC118, IC119, IC120, IC121, IC122, IC123, IC124, IC125, IC126, IC127, IC128, IC129, IC130, IC131, IC132, IC133, IC134, IC135, IC136, IC137, IC138, IC139, IC140, IC141, IC142, IC143, IC144, IC145, IC146, IC147, IC148, IC149, IC150, IC151, IC152, IC153, IC154, IC155, IC156, IC157, IC158, IC159, IC160, IC161, IC162, IC163, IC164, IC165, IC166, IC167, IC168, IC169, IC170, IC171, IC172, IC173, IC174, IC175, IC176, IC177, IC178, IC179, IC180, IC181, IC182, IC183, IC184, IC185, IC186, IC187, IC188, IC189, IC190, IC191, IC192, IC193, IC194, IC195, IC196, IC197, IC198, IC199, IC200, IC201, IC202, IC203, IC204, IC205, IC206, IC207, IC208, IC209, IC210, IC211, IC212, IC213, IC214, IC215, IC216, IC217, IC218, IC219, IC220, IC221, IC222, IC223, IC224, IC225, IC226, IC227, IC228, IC229, IC2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 | SMDLX0707RGBTR | SMD | SMDLX0707RGBTR | 285 | 1 | 285 | 300 | €0.29 | €86.70 | https://nl.mouser.com/ProductDetail/Lumex/SMD-LX0707RGB-TR?qs=u16ybLDytRYfAsx%252BT62puQ%3D%3D
COPASITOR | C1, C2, C3, C4, C5, C6, C7, C8, C9, C10, C11, C12, C13, C14, C15, C16, C17, C18, C19, C20, C21, C22, C23, C24, C25, C26, C27, C28, C29, C30, C31, C32, C33, C34, C35, C36, C37, C38, C39, C40, C41, C42, C43, C44, C45, C46, C47, C48, C49, C50, C51, C52, C53, C54, C55, C56, C57, C58, C59, C60, C61, C62, C63, C64, C65, C66, C67, C68, C69, C70, C71, C72, C73, C74, C75, C76, C77, C78, C79, C80, C81, C82, C83, C84, C85, C86, C87, C88, C89, C90, C91, C92, C93, C94, C95, C96, C97, C98, C99, C100, C101, C102, C103, C104, C105, C106, C107, C108, C109, C110, C111, C112, C113, C114, C115, C116, C117, C118, C119, C120, C121, C122, C123, C124, C125, C126, C127, C128, C129, C130, C131, C132, C133, C134, C135, C136, C137, C138, C139, C140, C141, C142, C143, C144, C145, C146, C147, C148, C149, C150, C151, C152, C153, C154, C155, C156, C157, C158, C159, C160, C161, C162, C163, C164, C165, C166, C167, C168, C169, C170, C171, C172, C173, C174, C175, C176, C177, C178, C179, C180, C181, C182, C183, C184, C185, C186, C187, C188, C189, C190, C191, C192, C193, C194, C195, C196, C197, C198, C199, C200, C201, C202, C203, C204, C205, C206, C207, C208, C209, C210, C211, C212, C213, C214, C215, C216, C217, C218, C219, C220, C221, C222, C223, C224, C225, C226, C227, C228, C229, C230, C231, C232, C233, C234, C235, C236, C237, C238, C239, C240, C241, C242, C243, C244, C245, C246, C247, C248, C249, C250, C251, C252, C253, C254, C255, C256, C257, C258, C259, C260, C261, C262, C263, C264, C265, C266, C267, C268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 | 1uf | SMD | 0603 | 285 | 1 | 285 | 300 | €0.06 | €18.30 | https://nl.mouser.com/ProductDetail/YAGEO/CS0603KPX7R7BB105?qs=A6eO%252BMLsxmT7hSNSnXASag%3D%3D
RESISTOR | R2, R3, R4, R5, R6 | 4.7Kohm | SMD | 0603 | 5 | 1 | 5 | 20 | €0.02 | €0.40 | https://nl.mouser.com/ProductDetail/YAGEO/RC0603FR-7W4K7L?qs=sGAEpiMZZMtlubZbdhIBIE8A1EWi7VIOGBYrsK7SDxM%3D
 |  |  |  |  |  |  |  |  |  | €0.00
RESISTOR | R1, | 47Kohm | SMD | 0603 | 1 | 1 | 1 | 10 | €0.03 | €0.30 | https://nl.mouser.com/ProductDetail/YAGEO/RT0603FRE1347KL?qs=sGAEpiMZZMtlubZbdhIBIE441mth93wmRkj7wzRubmY%3D
RESISTOR | R7 | 10Kohm | SMD | 0603 | 1 | 1 | 1 | 10 | €0.01 | €0.14 | https://nl.mouser.com/ProductDetail/TE-Connectivity-Holsworthy/CRGCQ0603F10K?qs=sGAEpiMZZMtlubZbdhIBIOInyB5Ysv8sj2Ll6mHEUxE%3D
IC | IC286 | AT42QT2120-MMHR | SMD | VQFN-20-1EP_3x3mm_P0.4mm_EP1.7x1.7mm | 1 | 1 | 1 | 2 | €1.68 | €3.36 | https://nl.mouser.com/ProductDetail/Microchip-Technology/AT42QT2120-MMHR?qs=B3NtdMthFzGgZrO0zDJykg%3D%3D
 |  |  |  |  |  |  |  |  |  | €109.20
 |  |  |  |  |  |  | Amount of PCBs | #REF! | Total: | €218.40

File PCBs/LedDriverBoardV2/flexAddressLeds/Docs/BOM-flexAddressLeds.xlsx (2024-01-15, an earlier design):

Catagory | Name in schematic: | Name/Value | Mounting type | Footprint: | Nr. per. PCB: | Amount of PCBs: | Total amount: | To order: | Price per.part: | Price total: | Link:
LED | D6,D4,D5,D3,D9,D7,D1,D8,D10,D2 | SK6812MINI | SMD | LED_SK6812MINI_PLCC4_3.5x3.5mm_P1.75mm | 5 | 2 | 10 | 10 | €0.46 | €4.60 | https://www.digikey.nl/en/products/detail/adafruit-industries-llc/2686/5804107?s=N4IgTCBcDaIMoGkBsAOAjGAsgSQHLZAF0BfIA
LED | D11,D19,D18,D14,D16,D13,D17,D15,D20,D12 | WS2812B | SMD | LED_WS2812B_PLCC4_5.0x5.0mm_P3.2mm | 5 | 2 | 10 | 50 | €0.52 | €26.00 | https://nl.mouser.com/ProductDetail/SparkFun/COM-16346?qs=OlC7AqGiEDnspdV1Dchx7w%3D%3D
LED | D30,D24,D21,D28,D22,D26,D27,D25,D29,D23 | SMD-LX0707RGB-TR | SMD | SMDLX0707RGBTR | 5 | 2 | 10 | 10 | €0.44 | €4.40 | https://nl.mouser.com/ProductDetail/Lumex/SMD-LX0707RGB-TR?qs=u16ybLDytRYfAsx%252BT62puQ%3D%3D
COPASITOR | C4,C11,C14,C12,C15,C6,C10,C9,C5,C8,C13,C7,C1,C2,C3 | 1uf | SMD | 0603 | 15 | 2 | 30 | 30 | €0.02 | €0.60 | https://nl.mouser.com/ProductDetail/KYOCERA-AVX/KGM15AR71C104KT?qs=Jm2GQyTW%2FbiNMH1Ynxi4nA%3D%3D
 |  |  |  |  |  |  | Amount of PCBs | #REF! | Total: | €35.60

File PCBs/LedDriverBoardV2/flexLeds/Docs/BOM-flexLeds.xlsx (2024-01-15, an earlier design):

Catagory | Name in schematic: | Name/Value | Mounting type | Footprint: | Nr. per. PCB: | Amount of PCBs: | Total amount: | To order: | Price per.part: | Price total: | Link:
LED | D6,D4,D5,D3,D9,D7,D1,D8,D10,D2 | RED | SMD | 0805 | 10 | 2 | 20 | 30 | €0.25 | €7.53 | https://nl.mouser.com/ProductDetail/Lite-On/LTST-C171KRKT?qs=5XMAZBf2SiSTcAb1f5vDzw%3D%3D
LED | D11,D19,D18,D14,D16,D13,D17,D15,D20,D12 | GREEN | SMD | 0805 | 10 | 2 | 20 | 30 | €0.21 | €6.42 | https://nl.mouser.com/ProductDetail/Lite-On/LTST-C171GKT?qs=DXsB9OwW3bmgO%252BU8es%2F20A%3D%3D
LED | D30,D24,D21,D28,D22,D26,D27,D25,D29,D23 | BLUE | SMD | 0805 | 10 | 2 | 20 | 30 | €0.29 | €8.64 | https://nl.mouser.com/ProductDetail/Lite-On/LTST-C171TBKT?qs=DIGZ1Yxiz2%2FRYShBNqRoMg%3D%3D
LED | LED8,LED7,LED5,LED6 | 150141M173100 | SMD | 150141M173100 | 4 | 2 | 8 | 10 | €0.46 | €4.60 | https://nl.mouser.com/ProductDetail/Wurth-Elektronik/150141M173100?qs=2kOmHSv6VfT%2Fmnpysgc7Ng%3D%3D
LED | LED3,LED4,LED2,LED1 | 19337CRSBHGHCA012T | SMD | 19337CRSBHGHCA012T | 4 | 2 | 8 | 10 | €0.30 | €3.00 | https://www.digikey.nl/en/products/detail/everlight-electronics-co-ltd/19-337C-RSBHGHC-A01-2T/8535285
SWITCH | SW2,SW1 | TL3342F260QG | SMD | TL3342F260QG | 2 | 2 | 4 | 5 | €0.61 | €3.05 | https://nl.mouser.com/ProductDetail/E-Switch/TL3342F260QG?qs=6C6BR4UgC3Of90YOH%2FEXyw%3D%3D
SWITCH | SW3,SW4 | TS174805YE160SMTTR | SMD | TS174805YE160SMTTR | 2 | 2 | 4 | 5 | €0.26 | €1.30 | https://nl.mouser.com/ProductDetail/CUI-Devices/TS17-48-05-YE-160-SMT-TR?qs=tlsG%2FOw5FFiMIbV0B74FuA%3D%3D
RESISTOR | R4, R5, R6 | 20ohm | SMD | 0805 | 3 | 2 | 6 | 10 | €0.05 | €0.47 | https://nl.mouser.com/ProductDetail/Panasonic/ERJ-P06J200V?qs=Zyl8A9hlmJp6FiObcOjnwA%3D%3D
RESISTOR | R1, R2, R3, R7, R8, R9 | 165ohm | SMD | 0805 | 6 | 2 | 12 | 20 | €0.16 | €3.20 | https://nl.mouser.com/ProductDetail/Panasonic/ERJ-P06F1650V?qs=iIVTEDlrHA1ep%2F%252BbygSiIA%3D%3D
 |  |  |  |  |  |  | Amount of PCBs | #REF! | Total: | €38.21

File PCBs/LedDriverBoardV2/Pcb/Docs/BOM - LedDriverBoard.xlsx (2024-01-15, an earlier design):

Catagory | Name in schematic: | Name/Value | Mounting type | Footprint: | Nr. per. PCB: | Amount of PCBs: | Total amount: | To order: | Price per.part: | Price total: | Link:
IOEXPANDER | U9,U8,U7 | PCA9670BS,118 | SMD | QFN50P300X300X100-17N-D | 3 | 2 | 6 | 8 | €1.55 | €12.40 | https://nl.mouser.com/ProductDetail/NXP-Semiconductors/PCA9670BS118?qs=LOCUfHb8d9vyec%2F1PtVhAw%3D%3D
LEDDRIVER | U4,U6,U5 | TLC59401RHBR | SMD | QFN50P500X500X100-33N-D | 3 | 2 | 6 | 8 | €2.53 | €20.24 | https://nl.mouser.com/ProductDetail/Texas-Instruments/TLC59401RHBR?qs=%2Fqzd9s%252BcLd5jLWxG9iB8xw%3D%3D
FLASH | U2 | IS25LP032D-JLLE | SMD | SON127P600X500X75-9N-D | 1 | 2 | 2 | 3 | €1.24 | €3.72 | https://nl.mouser.com/ProductDetail/ISSI/IS25LP032D-JLLE?qs=DXv0QSHKF4wnam7hnzWEbg%3D%3D
CONNECTOR | J4 | 1778641 | THT | SHDRRA4W60P0X250_1X4_1170X750X510P | 1 | 2 | 2 | 3 | €0.98 | €2.94 | https://nl.mouser.com/ProductDetail/Phoenix-Contact/1778641?qs=i0qWf6NAoDs%252BwkQoFV1ycQ%3D%3D
CONNECTOR | J6,J7 | 1778667 | THT | SHDRRA6W70P0X250_1X6_1670X750X510P | 2 | 2 | 4 | 5 | €1.43 | €7.15 | https://nl.mouser.com/ProductDetail/Phoenix-Contact/1778667?qs=i0qWf6NAoDtdrKZdTiVKlQ%3D%3D
GATEBUFFER | IC1 | SN74AHCT125DR | SMD | SOIC127P600X175-14N | 1 | 2 | 2 | 4 | €0.35 | €1.41 | https://nl.mouser.com/ProductDetail/Texas-Instruments/SN74AHCT125DR?qs=B7lSdIxWQkm9VQkJOjfRaA%3D%3D
RESISTOR | R4,R6 | 470 | SMD | 0603 | 2 | 2 | 4 | 10 | €0.01 | €0.10 | https://nl.mouser.com/ProductDetail/YAGEO/RC0603FR-10470RL?qs=EiqXWrxQq62gi8HBTlzDog%3D%3D
CAPACITOR | C26,C7,C29,C20,C19,C18,C25,C15,C27,C17,C30,C28,C23,C31 | 100nF | SMD | 0603 | 14 | 2 | 28 | 40 | €0.03 | €1.00 | https://nl.mouser.com/ProductDetail/KYOCERA-AVX/06035C104KAT2A?qs=wORnlwVG%2F0dQ8Y%2FnMEnCGg%3D%3D
RESISTOR | R31,R32,R30 | 2k | SMD | 0603 | 3 | 2 | 6 | 10 | €0.03 | €0.33 | https://nl.mouser.com/ProductDetail/Vishay-Draloric/RCG06032K00FKEA?qs=vOeJqewp7jAkaO2tUWtxNA%3D%3D
RESISTOR | R19,R16,R22,R34,R20,R35,R17,R23,R21,R18,R33 | 10k | SMD | 0603 | 11 | 2 | 22 | 30 | €0.02 | €0.48 | https://nl.mouser.com/ProductDetail/Bourns/CR0603AFX-1002EAS?qs=PzGy0jfpSMvnIWl2FjD7DQ%3D%3D
CONNECTOR | J5 | Conn_01x16_Pin | SMD | TE_1-84952-6_1x16-1MP_P1.0mm_Horizontal | 1 | 2 | 2 | 3 | €0.87 | €2.62 | https://nl.mouser.com/ProductDetail/TE-Connectivity/1-84952-6?qs=uUkeXfjQ8uRn%252Bu4rrhD4JA%3D%3D
RESISTOR | C10,C8 | 10uF | SMD | 1206 | 2 | 2 | 4 | 10 | €0.34 | €3.35 | https://nl.mouser.com/ProductDetail/KEMET/C1206C106K4RACTU?qs=guDyKOyRtV0mxqxQedB7kA%3D%3D
CONNECTOR | J2,J3,J1 | FFC3B1120T | SMD | FFC3B11-20-T | 3 | 2 | 6 | 10 | €0.32 | €3.18 | https://nl.mouser.com/ProductDetail/GCT/FFC3B11-20-T?qs=KUoIvG%2F9IlYkjs6FOujy%252BQ%3D%3D
RESISTOR | R11,R10,R8,R9 | 62 | SMD | 0603 | 4 | 2 | 8 | 10 | €0.02 | €0.20 | https://nl.mouser.com/ProductDetail/YAGEO/RE0603FRE0762RL?qs=fTsMJN6MUUv1sp9RVyQSKw%3D%3D
CAPACITOR | C9 | 4.7nF 1kV | SMD | 0805 | 1 | 2 | 2 | 10 | €0.19 | €1.94 | https://nl.mouser.com/ProductDetail/Walsin/0805B472K102CT?qs=hzBznG4dWXXfDjU4OfxUFQ%3D%3D
CAPACITOR | C3,C21,C4,C5,C13,C22,C16 | 10uF | SMD | 0603 | 7 | 2 | 14 | 20 | €0.10 | €1.92 | https://nl.mouser.com/ProductDetail/Murata-Electronics/GRM188C81C106MA73D?qs=W1gvEE3epjzPVR28V3qh%2Fw%3D%3D
LED | D4,D2 | GREEN | SMD | 0805 | 2 | 2 | 4 | 5 | €0.21 | €1.07 | https://nl.mouser.com/ProductDetail/Lite-On/LTST-C171GKT?qs=DXsB9OwW3bmgO%252BU8es%2F20A%3D%3D
RESISTOR | R5,R7,R2 | 330 | SMD | 0603 | 3 | 2 | 6 | 10 | €0.01 | €0.08 | https://nl.mouser.com/ProductDetail/SEI-Stackpole/RMCF0603FT330R?qs=FESYatJ8odLaN56qufdyJQ%3D%3D
RESISTOR | R25,R24 | 27 | SMD | 0603 | 2 | 2 | 4 | 10 | €0.03 | €0.26 | https://nl.mouser.com/ProductDetail/TE-Connectivity-Holsworthy/CRG0603F27R?qs=VHcS2MTj4gbfJ48omZvbHQ%3D%3D
FUSE | F3,F5,F2,F7,F8,F4,F1,F6 | 0,5A | SMD | 0805 | 8 | 2 | 16 | 20 | €0.15 | €3.02 | https://nl.mouser.com/ProductDetail/Bel-Fuse/0ZCK0020FF2G?qs=SRYZG9HaIQ1YaXTwF3oUbw%3D%3D
CRYSTAL | Y1 | 32.768mHz | SMD | Crystal_SMD_3215-2Pin_3.2x1.5mm | 1 | 2 | 2 | 4 | €0.38 | €1.53 | https://nl.mouser.com/ProductDetail/Seiko-Semiconductors/SC32S-7PF20PPM?qs=3CPZD7qAgigZSR1ASVAS6w%3D%3D
DIODE | D8 | SSA33LHE3_A/H | SMD | DO-214AC-2 | 1 | 2 | 2 | 4 | €0.40 | €1.60 | https://nl.mouser.com/ProductDetail/Vishay-General-Semiconductor/SSA33LHE3_A-H?qs=asPD7ZL2j3W%252BZAXlcypYXg%3D%3D
LED | D1 | BLUE | SMD | 0805 | 1 | 2 | 2 | 3 | €0.29 | €0.86 | https://nl.mouser.com/ProductDetail/Lite-On/LTST-C171TBKT?qs=DIGZ1Yxiz2%2FRYShBNqRoMg%3D%3D
LED | D3 | RED | SMD | 0805 | 1 | 2 | 2 | 3 | €0.25 | €0.75 | https://nl.mouser.com/ProductDetail/Lite-On/LTST-C171KRKT?qs=5XMAZBf2SiSTcAb1f5vDzw%3D%3D
FUSE | F9 | - | SMD | 0031.7701.11 | 1 | 2 | 2 | 3 | €1.29 | €3.87 | https://nl.mouser.com/ProductDetail/Schurter/0031.7701.11
FUSE | - | 2.5A | SMD | OMF 125 | 1 | 2 | 2 | 4 | €0.75 | €3.01 | https://nl.mouser.com/ProductDetail/Schurter/3404.0013.11?qs=ar9f0rk5DXDlCixAsLqc7w%3D%3D
CAPACITOR | C12 | 1uF | SMD | 1206 | 1 | 2 | 2 | 10 | €0.01 | €0.05 | https://nl.mouser.com/ProductDetail/Samsung-Electro-Mechanics/CL31B105KOFNNNE?qs=349EhDEZ59o%252Bj%2FvC1Fmg0w%3D%3D
CAPACITOR | C6,C14 | 1uF | SMD | 0603 | 2 | 2 | 4 | 10 | €0.02 | €0.21 | https://nl.mouser.com/ProductDetail/KYOCERA-AVX/KGM15AR71C104KT?qs=Jm2GQyTW%2FbiNMH1Ynxi4nA%3D%3D
CAPACITOR | C24 | 4.7uF | SMD | 0603 | 1 | 2 | 2 | 10 | €0.06 | €0.59 | https://nl.mouser.com/ProductDetail/Samsung-Electro-Mechanics/CL10A475KO8NNNC?qs=X6jEic%2FHinAbIjmLnFfqqQ%3D%3D
RESISTOR | R1,R15,R12,R14,R3,R13 | 4.7k | SMD | 0603 | 6 | 2 | 12 | 20 | €0.06 | €1.22 | https://nl.mouser.com/ProductDetail/Welwyn-Components-TT-Electronics/WCR0603-4K7FI?qs=mbEfOQsdCzfBCmdhoNRGyQ%3D%3D
LDO | U3 | AP2112K-3.3 | SMD | SOT-23-5 | 1 | 2 | 2 | 4 | €0.33 | €1.30 | https://nl.mouser.com/ProductDetail/Diodes-Incorporated/AP2112K-3.3TRG1?qs=x6A8l6qLYDDPYHosCdzh%2FA%3D%3D
FERRITE | FB1,FB2 | FerriteBead | SMD | 0805 | 2 | 2 | 4 | 10 | €0.10 | €1.02 | https://nl.mouser.com/ProductDetail/TDK/MPZ2012S101AT000?qs=pLY5GE0xrmKpe1XYPmVCHA%3D%3D
RESISTOR | R26 | 1M | SMD | 0603 | 1 | 2 | 2 | 10 | €0.01 | €0.08 | https://nl.mouser.com/ProductDetail/SEI-Stackpole/RMCF0603FT1M00?qs=FESYatJ8odJNClY0wUC1cg%3D%3D
SWITCH | SW1,SW2,SW4,SW3 | SW_Push | SMD | SW_SPST_B3U-1000P | 4 | 2 | 8 | 10 | €0.85 | €8.53 | https://nl.mouser.com/ProductDetail/Omron-Electronics/B3U-1000P?qs=AO7BQMcsEu4ip80xyf2FwA%3D%3D
USB | J9 | USB_C_Receptacle_USB2.0 | SMD | USB_C_Receptacle_HRO_TYPE-C-31-M-12 | 1 | 2 | 2 | 4 | €0.84 | €3.35 | https://nl.mouser.com/ProductDetail/Molex/217179-0001?qs=DRkmTr78QAQqCH4BoIR1xg%3D%3D
ESD | D7 | PRTR5V0U2X | SMD | SOT-143 | 1 | 2 | 2 | 4 | €0.05 | €0.19 | https://nl.mouser.com/ProductDetail/Nexperia/PRTR5V0U2X215?qs=LOCUfHb8d9sDkgY4cRj8Lw%3D%3D
PHY | U1 | ATSAMD21J18A-M | SMD | QFN-64-1EP_9x9mm_P0.5mm_EP4.7x4.7mm | 1 | 2 | 2 | 3 | €3.99 | €11.97 | https://nl.mouser.com/ProductDetail/Microchip-Technology/ATSAMD21J18A-MU?qs=KLFHFgXTQiA5nYxZpqmjnQ%3D%3D
RESISTOR | R28,R29 | 5.1k 1% | SMD | 0603 | 2 | 2 | 4 | 10 | €0.01 | €0.15 | https://nl.mouser.com/ProductDetail/Bourns/CR0603AFX-5101EAS?qs=PzGy0jfpSMub%2Fi7zoEnwAw%3D%3D
CAPACITOR | C2,C1 | 2pF | SMD | 0402 | 2 | 2 | 4 | 10 | €0.17 | €1.70 | https://nl.mouser.com/ProductDetail/KYOCERA-AVX/0402YA2R0CAT2A?qs=cnDM9bjyeUi8ihqvIXYxow%3D%3D
CONNECTOR | J10 | Conn_01x02_Socket | THT | TerminalBlock_Phoenix_PT-1,5-2-3.5-H_1x02_P3.50mm_Horizontal | 1 | 2 | 2 | 3 | €0.54 | €1.62 | https://nl.mouser.com/ProductDetail/Phoenix-Contact/1984617?qs=ATjOrvm3mOhUrGlJQoUcpQ%3D%3D
CAPACITOR | C11 | 100uF | SMD | 0805 | 1 | 2 | 2 | 10 | €0.11 | €1.06 | https://nl.mouser.com/ProductDetail/KEMET/C0805C104K4RECAUTO?qs=MLItCLRbWswQcXlGMGaWig%3D%3D
LED | D5 | ORANGE | SMD | 0805 | 1 | 2 | 2 | 4 | €0.25 | €1.00 | https://nl.mouser.com/ProductDetail/Lite-On/LTST-C170KFKT?qs=gKd32bbgGM%2FWUWN9MKaKoA%3D%3D
RESISTOR | R27 | 100k | SMD | 0603 | 1 | 2 | 2 | 10 | €0.04 | €0.35 | https://nl.mouser.com/ProductDetail/Vishay-Draloric/RCG0603100KFKEA?qs=f%2F0S6rTelyXH%2FpVkET7riQ%3D%3D
NEOPIXEL | D6 | WS2812B | SMD | LED_WS2812B_PLCC4_5.0x5.0mm_P3.2mm | 1 | 2 | 2 | 4 |  | €0.00
 |  |  |  |  |  |  | Amount per PCB | €56.72 | Total: | €113.43

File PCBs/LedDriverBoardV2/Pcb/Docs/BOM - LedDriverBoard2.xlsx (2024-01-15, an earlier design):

Id | Designator | Footprint | Quantity | Designation | Supplier and ref
1 | R4,R6 | R_0603_1608Metric_Pad0.98x0.95mm_HandSolder | 2 | 470
2 | C26,C7,C29,C20,C19,C18,C25,C15,C27,C17,C30,C28,C23,C31 | C_0603_1608Metric_Pad1.08x0.95mm_HandSolder | 14 | 100nF
3 | H2,H4,H1,H3 | MountingHole_3.2mm_M3_DIN965 | 4 | MountingHole
4 | C3,C21,C4,C5,C13,C22,C16 | C_0603_1608Metric_Pad1.08x0.95mm_HandSolder | 7 | 10uF
5 | R31,R32,R30 | R_0603_1608Metric_Pad0.98x0.95mm_HandSolder | 3 | 2k
6 | R19,R16,R22,R34,R20,R35,R17,R23,R21,R18,R33 | R_0603_1608Metric_Pad0.98x0.95mm_HandSolder | 11 | 10k
7 | J5 | TE_1-84952-6_1x16-1MP_P1.0mm_Horizontal | 1 | Conn_01x16_Pin
8 | U4,U6,U5 | QFN50P500X500X100-33N-D | 3 | TLC59401RHBR
9 | C10,C8 | C_1206_3216Metric_Pad1.33x1.80mm_HandSolder | 2 | 10uF | >jelle
10 | J9 | USB_C_Receptacle_HRO_TYPE-C-31-M-12 | 1 | USB_C_Receptacle_USB2.0
11 | J2,J3,J1 | FFC3B1120T | 3 | FFC3B11-20-T
12 | R11,R10,R8,R9 | R_0603_1608Metric_Pad0.98x0.95mm_HandSolder | 4 | 62
13 | JP2,JP1 | SolderJumper-2_P1.3mm_Open_RoundedPad1.0x1.5mm | 2 | Jumper_2_Open
14 | D4,D2 | LED_0805_2012Metric_Pad1.15x1.40mm_HandSolder | 2 | GREEN
15 | R5,R7,R2 | R_0603_1608Metric_Pad0.98x0.95mm_HandSolder | 3 | 330
16 | R25,R24 | R_0603_1608Metric_Pad0.98x0.95mm_HandSolder | 2 | 27
17 | F3,F5,F2,F7,F8,F4,F1,F6 | Fuse_0805_2012Metric_Pad1.15x1.40mm_HandSolder | 8 | Polyfuse
18 | U9,U8,U7 | QFN50P300X300X100-17N-D | 3 | PCA9670BS,118
19 | Y1 | Crystal_SMD_3215-2Pin_3.2x1.5mm | 1 | 32.768mHz
20 | D8 | D_SMB_Handsoldering | 1 | D_Schottky
21 | J6,J7 | SHDRRA6W70P0X250_1X6_1670X750X510P | 2 | 1778667
22 | SW1,SW2,SW4,SW3 | SW_SPST_B3U-1000P | 4 | SW_Push | >johan
23 | D1 | LED_0805_2012Metric_Pad1.15x1.40mm_HandSolder | 1 | BLUE
24 | D3 | LED_0805_2012Metric_Pad1.15x1.40mm_HandSolder | 1 | RED
25 | F9 | 0031.7701.11 | 1 | Fuse | >jumper
26 | C12 | C_1206_3216Metric_Pad1.33x1.80mm_HandSolder | 1 | 1uF
27 | C6,C14 | C_0603_1608Metric_Pad1.08x0.95mm_HandSolder | 2 | 1uF
28 | JP3,JP5,JP4 | SolderJumper-3_P1.3mm_Open_RoundedPad1.0x1.5mm | 3 | Jumper_3_Open
29 | IC1 | SOIC127P600X175-14N | 1 | SN74AHCT125DR
30 | FB1,FB2 | L_0805_2012Metric_Pad1.15x1.40mm_HandSolder | 2 | FerriteBead
31 | C24 | C_0603_1608Metric_Pad1.08x0.95mm_HandSolder | 1 | 4.7uF
32 | R1,R15,R12,R14,R3,R13 | R_0603_1608Metric_Pad0.98x0.95mm_HandSolder | 6 | 4.7k
33 | U3 | SOT-23-5 | 1 | AP2112K-3.3
34 | J8 | 2X5-PTH-1.27MM | 1 | CORTEX_DEBUGPTH
35 | D7 | SOT-143 | 1 | PRTR5V0U2X
36 | U1 | QFN-64-1EP_9x9mm_P0.5mm_EP4.7x4.7mm | 1 | ATSAMD21J18A-M
37 | R28,R29 | R_0603_1608Metric_Pad0.98x0.95mm_HandSolder | 2 | 5.1k 1%
38 | C2,C1 | C_0402_1005Metric_Pad0.74x0.62mm_HandSolder | 2 | 22pF
39 | FID1,FID2,FID3 | Fiducial_1mm_Mask2mm | 3 | Fiducial
40 | J10 | TerminalBlock_Phoenix_PT-1,5-2-3.5-H_1x02_P3.50mm_Horizontal | 1 | Conn_01x02_Socket | >jelle
41 | C11 | C_0805_2012Metric_Pad1.18x1.45mm_HandSolder | 1 | 100uF
42 | D5 | LED_0805_2012Metric_Pad1.15x1.40mm_HandSolder | 1 | ORANGE
43 | R27 | R_0603_1608Metric_Pad0.98x0.95mm_HandSolder | 1 | 100k
44 | C9 | C_0805_2012Metric_Pad1.18x1.45mm_HandSolder | 1 | 4.7nF 1kV
45 | U2 | SON127P600X500X75-9N-D | 1 | IS25LP032D-JLLE | >?
46 | D6 | LED_WS2812B_PLCC4_5.0x5.0mm_P3.2mm | 1 | WS2812B
47 | J4 | SHDRRA4W60P0X250_1X4_1170X750X510P | 1 | 1778641
48 | R26 | R_0603_1608Metric_Pad0.98x0.95mm_HandSolder | 1 | 1m

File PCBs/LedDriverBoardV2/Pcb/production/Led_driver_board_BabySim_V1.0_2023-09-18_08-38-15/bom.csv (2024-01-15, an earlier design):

Designator | Footprint | Quantity | Value | LCSC Part #
C1, C2 | 0402 | 2 | 22pF
C10, C13, C18, C19 | 0603 | 4 | 10uF
C11, C3 | 0603 | 2 | 1uF
C12, C14, C15, C16, C17, C20, C22, C23, C24, C25, C26, C27, C28, C4 | 0603 | 14 | 100nF
C21 | 0603 | 1 | 4.7uF
C5, C8 | 1206 | 2 | 10uF
C6 | 0805 | 1 | 4.7nF 1kV
C7 | 0805 | 1 | 100uF
C9 | 1206 | 1 | 1uF
D1 | 0805 | 1 | BLUE
D2, D4 | 0805 | 2 | GREEN
D3 | 0805 | 1 | RED
D5 | 0805 | 1 | ORANGE
D6 | LED_WS2812B_PLCC4_5.0x5.0mm_P3.2mm | 1 | WS2812B
D7 | D_SOD-923 | 1 | ESD9B5.0ST5G
D8 | SOT-143 | 1 | PRTR5V0U2X
D9 | D_SMB_Handsoldering | 1 | D_Schottky
F1, F2, F3, F4 | 0805 | 4 | Polyfuse
F5 | 0031.7701.11 | 1 | Fuse
FB1, FB2 | 0805 | 2 | FerriteBead
FID1, FID2, FID3 | Fiducial_1mm_Mask2mm | 3 | Fiducial
H1, H2, H3, H4 | MountingHole_3.2mm_M3_DIN965 | 4 | MountingHole
IC1 | SOIC127P600X175-14N | 1 | SN74AHCT125DR
J1, J2, J3 | FFC3B1120T | 3 | FFC3B11-20-T
J10 | USB_Mini-B_Wuerth_65100516121_Horizontal | 1 | USB_B_Mini
J11 | TerminalBlock_Phoenix_PT-1,5-2-3.5-H_1x02_P3.50mm_Horizontal | 1 | Conn_01x02_Socket
J4 | TE_1-84952-6_1x16-1MP_P1.0mm_Horizontal | 1 | Conn_01x16_Pin
J5, J6 | SHDRRA6W70P0X250_1X6_1670X750X510P | 2 | 1778667
J7 | 2X3_POGO | 1 | M03X2POGO_PINS
J8 | SHDRRA4W60P0X250_1X4_1170X750X510P | 1 | 1778641
J9 | 2X5-PTH-1.27MM | 1 | CORTEX_DEBUGPTH
JP1, JP2 | SolderJumper-2_P1.3mm_Open_RoundedPad1.0x1.5mm | 2 | Jumper_2_Open
JP3, JP4, JP5 | SolderJumper-3_P1.3mm_Bridged2Bar12_RoundedPad1.0x1.5mm | 3 | Jumper_3_Bridged12
R1, R12, R13, R15, R16, R3 | 0603 | 6 | 4.7k
R10, R11, R8, R9 | 0603 | 4 | 62
R14, R17 | 0603 | 2 | 10k
R18, R19 | 0603 | 2 | 27
R2, R5, R7 | 0603 | 3 | 330
R20 | 0603 | 1 | 1M
R21 | 0603 | 1 | 100k
R22, R23, R24 | 0603 | 3 | 2k
R4, R6 | 0603 | 2 | 470
SW1 | PTS810SJG250SMTRLFS | 1 | SW_Push
U1 | QFN-64-1EP_9x9mm_P0.5mm_EP4.7x4.7mm | 1 | ATSAMD21J18A-M
U2 | SON127P600X500X75-9N-D | 1 | IS25LP032D-JLLE
U3 | SOT-23-5 | 1 | AP2112K-3.3
U4, U5, U6 | QFN50P500X500X100-33N-D | 3 | TLC59401RHBR
U7, U8, U9 | QFN50P300X300X100-17N-D | 3 | PCA9670BS,118
Y1 | Crystal_SMD_3215-2Pin_3.2x1.5mm | 1 | 32.768mHz

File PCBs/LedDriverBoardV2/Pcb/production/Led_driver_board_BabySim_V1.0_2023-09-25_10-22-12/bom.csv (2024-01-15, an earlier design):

Designator | Footprint | Quantity | Value | LCSC Part #
C1, C2 | 0402 | 2 | 2pF
C10, C8 | 1206 | 2 | 10uF
C11 | 0805 | 1 | 100uF
C12 | 1206 | 1 | 1uF
C13, C16, C21, C22, C3, C4, C5 | 0603 | 7 | 10uF
C14, C6 | 0603 | 2 | 1uF
C15, C17, C18, C19, C20, C23, C25, C26, C27, C28, C29, C30, C31, C7 | 0603 | 14 | 100nF
C24 | 0603 | 1 | 4.7uF
C9 | 0805 | 1 | 4.7nF 1kV
D1 | 0805 | 1 | BLUE
D2, D4 | 0805 | 2 | GREEN
D3 | 0805 | 1 | RED
D5 | 0805 | 1 | ORANGE
D6 | LED_WS2812B_PLCC4_5.0x5.0mm_P3.2mm | 1 | WS2812B
D7 | SOT-143 | 1 | PRTR5V0U2X
D8 | DIOM5127X229N | 1 | D_Schottky
F1, F2, F3, F4, F5, F6, F7, F8 | 0805 | 8 | Polyfuse
F9 | 0031.7701.11 | 1 | Fuse
FB1, FB2 | 0805 | 2 | FerriteBead
FID1, FID2, FID3 | Fiducial_1mm_Mask2mm | 3 | Fiducial
H1, H2, H3, H4 | MountingHole_3.2mm_M3_DIN965 | 4 | MountingHole
IC1 | SOIC127P600X175-14N | 1 | SN74AHCT125DR
J1, J2, J3 | FFC3B1120T | 3 | FFC3B11-20-T
J10 | TerminalBlock_Phoenix_PT-1,5-2-3.5-H_1x02_P3.50mm_Horizontal | 1 | Conn_01x02_Socket
J4 | SHDRRA4W60P0X250_1X4_1170X750X510P | 1 | 1778641
J5 | TE_1-84952-6_1x16-1MP_P1.0mm_Horizontal | 1 | Conn_01x16_Pin
J6, J7 | SHDRRA6W70P0X250_1X6_1670X750X510P | 2 | 1778667
J8 | 2X5-PTH-1.27MM | 1 | CORTEX_DEBUGPTH
J9 | USB_C_Receptacle_HRO_TYPE-C-31-M-12 | 1 | USB_C_Receptacle_USB2.0
JP1, JP2 | SolderJumper-2_P1.3mm_Open_RoundedPad1.0x1.5mm | 2 | Jumper_2_Open
JP3, JP4, JP5 | SolderJumper-3_P1.3mm_Open_RoundedPad1.0x1.5mm | 3 | Jumper_3_Open
R1, R12, R13, R14, R15, R3 | 0603 | 6 | 4.7k
R10, R11, R8, R9 | 0603 | 4 | 62
R16, R17, R18, R19, R20, R21, R22, R23, R33, R34, R35 | 0603 | 11 | 10k
R2, R5, R7 | 0603 | 3 | 330
R24, R25 | 0603 | 2 | 27
R26 | 0603 | 1 | 1m
R27 | 0603 | 1 | 100k
R28, R29 | 0603 | 2 | 5.1k 1%
R30, R31, R32 | 0603 | 3 | 2k
R4, R6 | 0603 | 2 | 470
SW1, SW2, SW3, SW4 | SW_SPST_B3U-1000P | 4 | SW_Push
U1 | QFN-64-1EP_9x9mm_P0.5mm_EP4.7x4.7mm | 1 | ATSAMD21J18A-M
U2 | SON127P600X500X75-9N-D | 1 | IS25LP032D-JLLE
U3 | SOT-23-5 | 1 | AP2112K-3.3
U4, U5, U6 | QFN50P500X500X100-33N-D | 3 | TLC59401RHBR
U7, U8, U9 | QFN50P300X300X100-17N-D | 3 | PCA9670BS,118
Y1 | Crystal_SMD_3215-2Pin_3.2x1.5mm | 1 | 32.768mHz

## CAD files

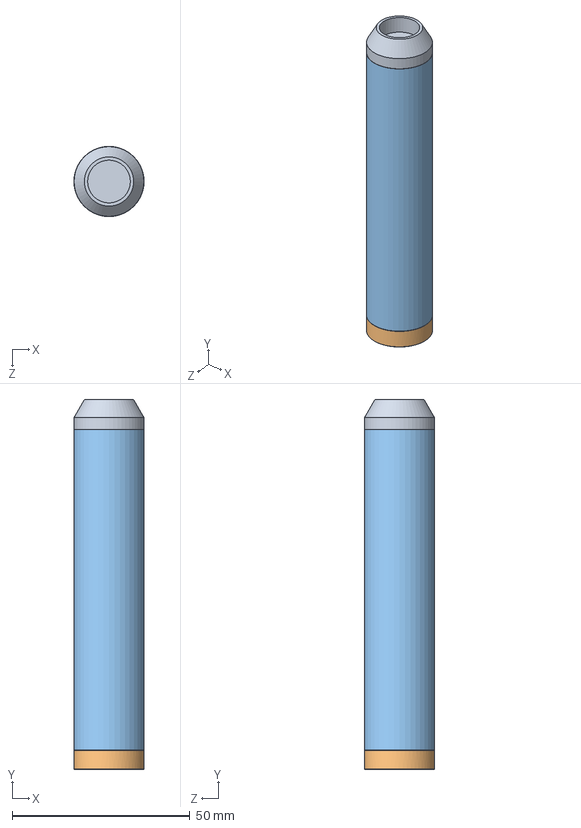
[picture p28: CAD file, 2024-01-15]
Pi_Spectrometer/Cad/spectroscope/spectroscope.SLDASM
19.8 x 104.0 x 19.8 mm
back
front
middle

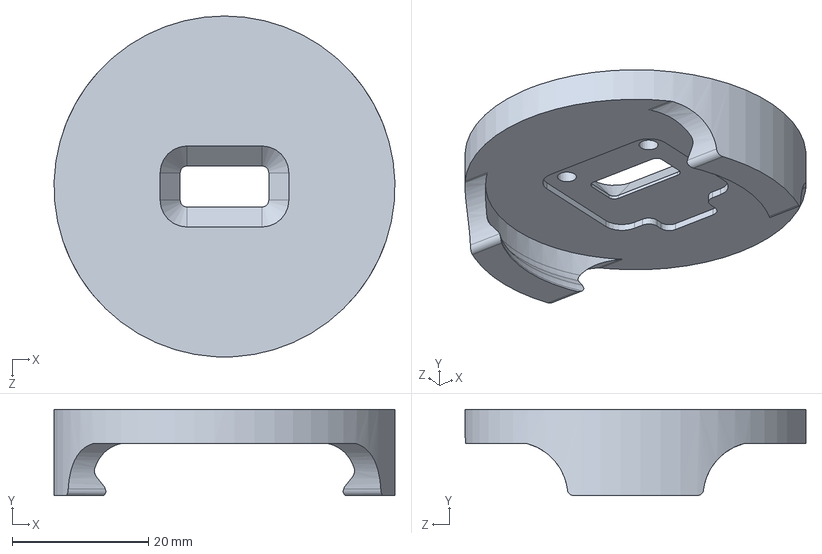
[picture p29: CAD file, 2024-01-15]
Arduino_Spectrometer/Cad/AS7341 sensorHousing.SLDPRT
50.0 x 12.7 x 50.0 mm

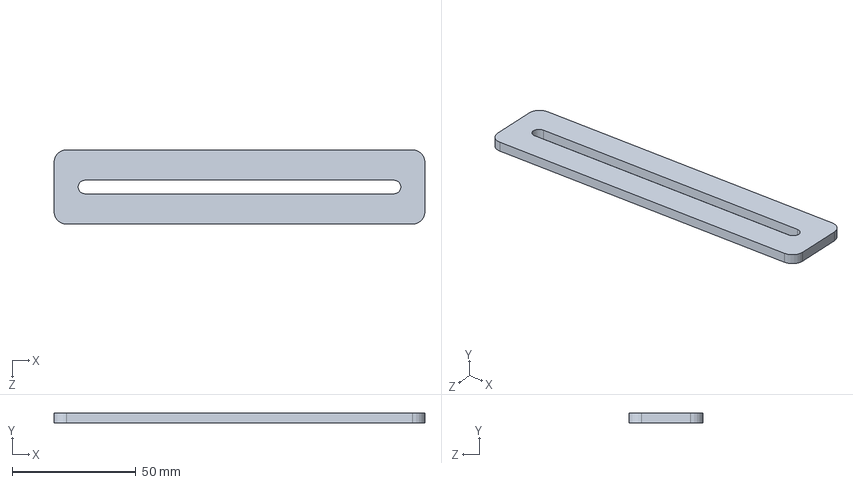
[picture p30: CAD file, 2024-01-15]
Pi_Spectrometer/Cad/party plate.SLDPRT
150.0 x 4.00 x 30.0 mm

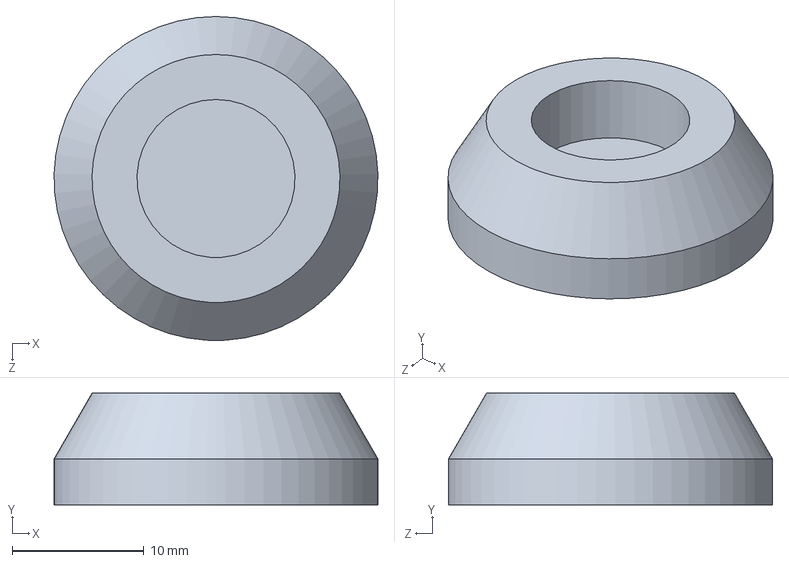
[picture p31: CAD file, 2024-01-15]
Pi_Spectrometer/Cad/spectroscope/back.SLDPRT
24.6 x 8.50 x 24.6 mm

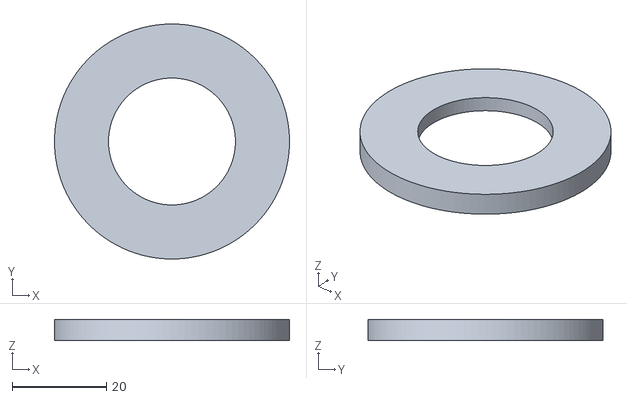
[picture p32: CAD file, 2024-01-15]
Arduino_Spectrometer/Cad/sensorHousing.stl
50.0 x 50.0 x 4.57

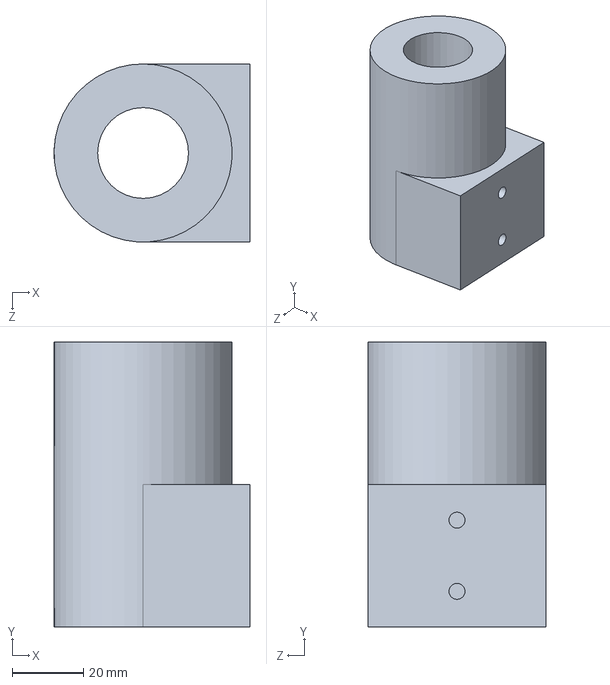
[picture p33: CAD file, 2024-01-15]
Pi_Spectrometer/Cad/Spectrometer holder.SLDPRT
55.0 x 80.0 x 50.0 mm

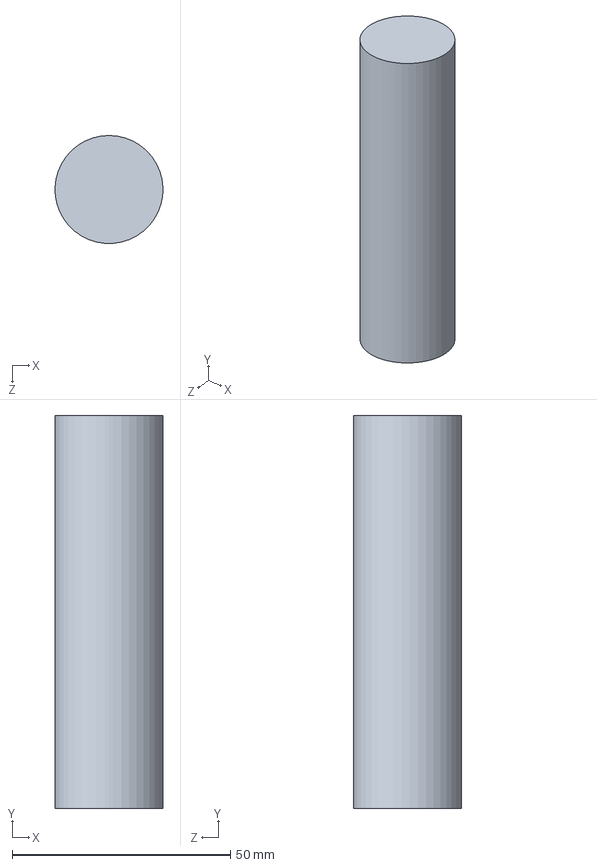
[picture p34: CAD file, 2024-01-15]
Pi_Spectrometer/Cad/spectroscope/middle.SLDPRT
24.7 x 90.0 x 24.8 mm

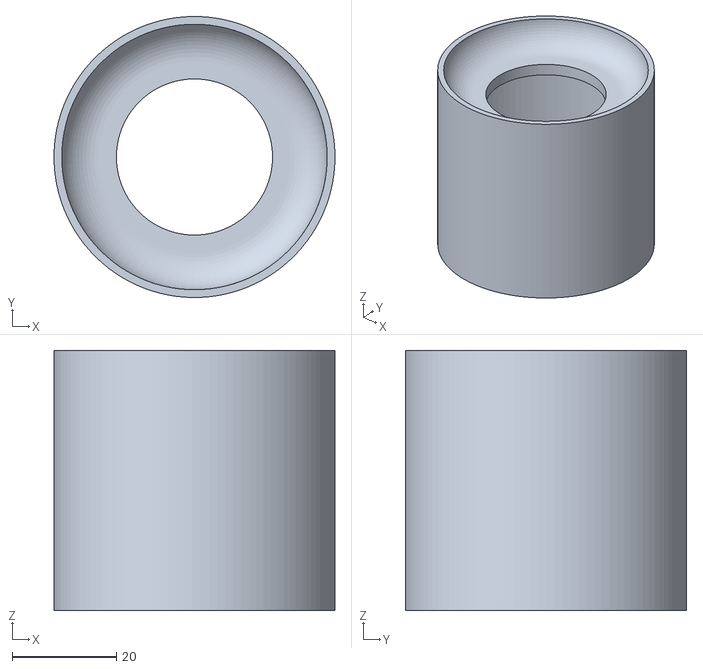
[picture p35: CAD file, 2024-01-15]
Arduino_Spectrometer/Cad/sampleHousing.stl
54.0 x 54.0 x 50.0

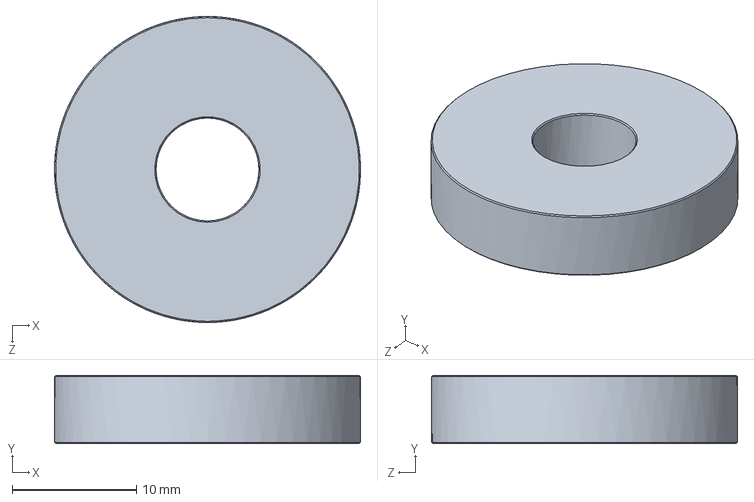
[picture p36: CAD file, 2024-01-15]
Pi_Spectrometer/Cad/spectroscope/front.SLDPRT
24.6 x 5.50 x 24.6 mm

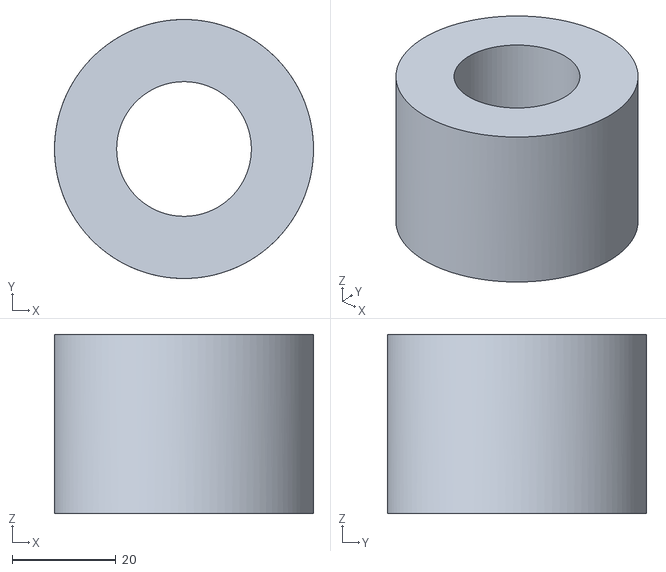
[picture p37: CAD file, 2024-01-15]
Arduino_Spectrometer/Cad/spectoHouder.stl
50.0 x 50.0 x 34.6

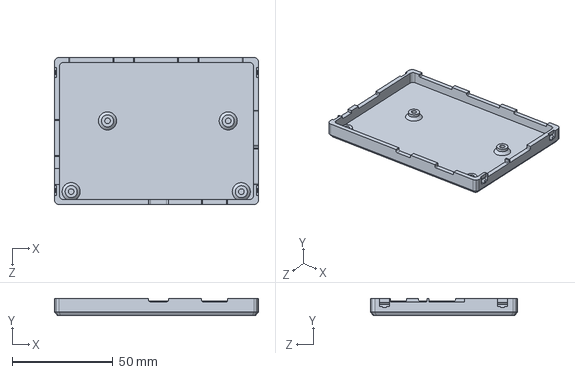
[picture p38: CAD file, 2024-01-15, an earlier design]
PCBs/LedDriverBoardV2/Cad/LedDriverBoard_Case_Option1/bottom.SLDPRT
101.0 x 8.50 x 73.0 mm

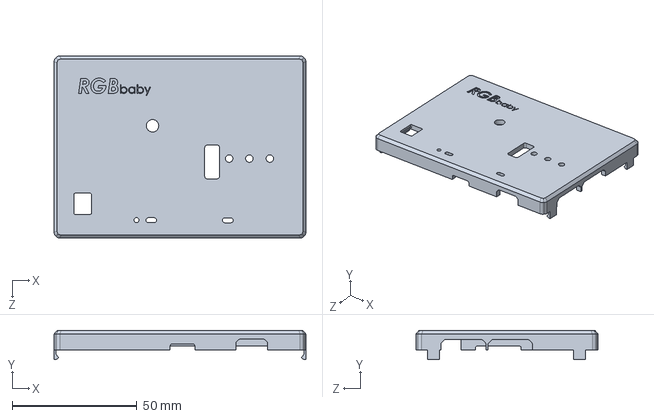
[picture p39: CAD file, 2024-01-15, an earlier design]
PCBs/LedDriverBoardV2/Cad/LedDriverBoard_Case_Option1/top.SLDPRT
101.0 x 11.8 x 73.0 mm

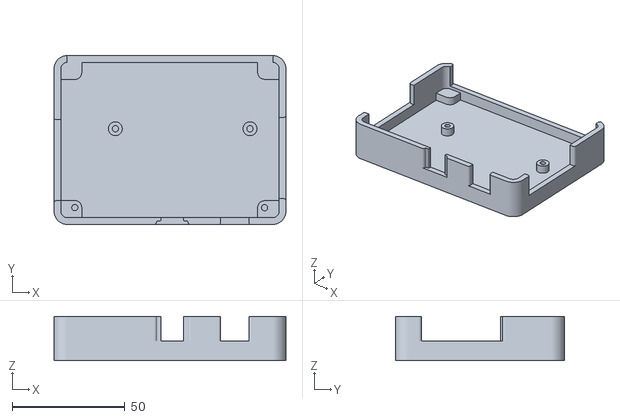
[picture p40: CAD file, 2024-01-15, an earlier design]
PCBs/LedDriverBoardV2/Cad/LedDriverBoard_Case_Option2/case-bottom.stl
103.0 x 75.0 x 19.6

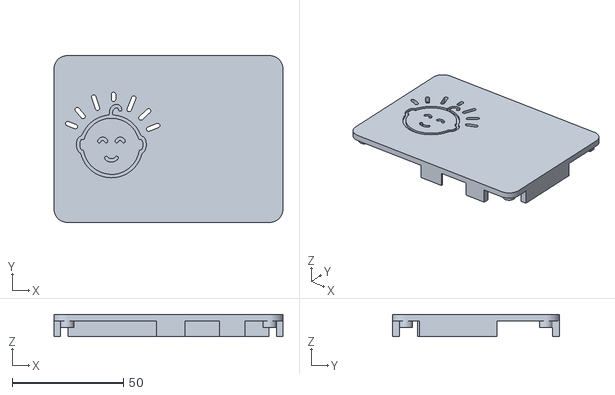
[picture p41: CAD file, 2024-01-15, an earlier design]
PCBs/LedDriverBoardV2/Cad/LedDriverBoard_Case_Option2/case-top.stl
103.0 x 75.0 x 10.0

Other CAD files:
PCBs/LedDriverBoardV2/Cad/LedDriverBoard_Case_Option2/Spectrometer holder.STL
PCBs/LedDriverBoardV2/Cad/LedDriverBoard_Case_Option2/party plate.STL
PCBs/LedDriverBoardV2/Cad/LedDriverBoard_Case_Option2/bottom.STL
PCBs/LedDriverBoardV2/Cad/LedDriverBoard_Case_Option2/top.STL
Arduino_Spectrometer/Cad/AS7341 sensorHousing.STL

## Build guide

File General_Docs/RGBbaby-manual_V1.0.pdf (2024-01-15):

# RGBbaby – manual

By Emiel Visser and Joris Bol

DOCUMENT ORGANISATIONAL DETAILS:
Document type:
Skills consultant: | Paul van Wegen
Project client: | Johan Korten
Education: | Embedded Systems Engineering
Institute: | School of Engineering and Automotive, Hogeschool Arnhem-Nijmegen
Report date: | 9-1-2024
Report version: | v1.0
Project duration: | Semester 3
Education term:
Students: | 2111740 (Emiel Visser), 2108100 (Joris Bol)

Embedded Systems Engineering · HAN University of Applied Sciences

## Version management

Version | Date | Change | Name
V1.0 | 11-9-2023 | Creation document, preface, C1, C2 & C3. | J. Bol
V1.0 | 12-11-2023 | Added programming environment tab. | E. Visser
V1.0 | 20-11-2023 | Added spectrometer tab. | J. Bol
V1.0 | 04-01-2024 | Added more information in the hardware section. | E. Visser
V1.0 | 05-01-2024 | Added more information in the hardware section. | E. Visser
V1.0 | 06-01-2024 | Added more information in the hardware section. | E. Visser
V1.0 | 07-01-2024 | Added more info in the hardware and debugging section. | E. Visser
V1.0 | 09-01-2024 | Added bibliography, performed spellcheck. | E. Visser

## Table of contents

Version management | 2
Preface | 5
1 – KiCad setup | 6
2 – Programming environment | 8
2.1 – Visual studio code | 8
2.2 – Clion | 8
2.2.1 – Get a JetBrains licence | 8
2.2.2 – Install Clion | 8
2.2.3 – Install Arm GNU toolchain | 8
2.2.4 – Cloning git repository | 9
2.2.5 – Setting up IDE | 10
2.2.6 – Setting up toolchain | 11
2.2.7 – Configuring CMake | 11
2.3 – Flashing and debugging | 13
2.3.1 – ledDriverBoardV2: | 13
2.3.2 – LedDriverBoardV3: | 15
3 – Hardware | 18
3.1 – LedDriverBoardV2 | 18
3.1.1 – Power: | 18
3.1.2 – First power up: | 18
3.1.3 – Programming: | 18
3.1.4 – Inputs: | 18
3.1.5 – Busses: | 18
3.1.6 – Outputs: | 19
3.1.7 – Jumper selections: | 19
3.1.8 – Problems: | 19
3.1.9 – Things to lookout for: | 20
3.2 – FlexledsV1.0 | 20
3.2.1 – Connecting the flex PCB: | 20
3.3 – flexAddresLedsV1.0 | 22
3.3.1 – Connecting the flex PCB: | 22
3.4 – LedDriverBoardV3 | 24
3.4.1 – Power: | 24
3.4.2 – First power up: | 24
3.4.3 – Programming: | 24

3.4.4 – Inputs: | 24
3.4.5 – Busses: | 24
3.4.6 – Outputs: | 25
3.4.7 – Jumper selections: | 25
3.4.8 – Problems: | 25
3.4.9 – Things to lookout for: | 25
3.5 – flexAddressLedsV2.3 | 26
3.5.1 – Connecting the flex PCB: | 26
4 – Testing setup | 28
4.1 – PySpectrometer | 28
4.1.1 – Initial setup | 28
4.1.2 – Installing the necessary software | 29
4.1.3 – Running the program | 29
4.1.4 – Hardware | 29
5 – Documents and documentation method | 30
6 – Bibliography | 31

## Preface

This document is meant for the successors of this project. In this document, you will find helpful installation guides and other useful instructions. Chapter 1, 2 and 3 are written in tutorial style, containing a step-by-step process of how you can set up your working environment and how to work with the PCBs we made. The following chapter explains our way of working and how you can build upon it. Chapter 5 contains an explanation of our workflow and were and what we documented. This document is strictly meant to help guide you in the setup of your work environment and not as a project guide.

Project summary
RGBbaby is a project that came in to being because of an S3 project. The Wilhelmina kinderziekenhuis (WKZ) is the client and Johan Korten the product owner. J. Korten is developing a basic life support doll for the hospital based on an already existing CPR baby doll. This project together with other projects inside the Health Concept Lab inside the HAN are meant to expand upon the doll and make it an advanced life support doll.

Our project is specifically focusing on the colour changing abilities of the skin. This meant that we had to develop an actuator and a new skin for the baby. There already was some research done on this topic by other students regarding the skin of the baby, sadly we found this research to be insufficient, so we redid most of it ourselves.

There was no previous research done on the led topic, so this had to be done from the start. Due to research done by another student, there was no certainty on the final form factor of the product, so we had to stay as modular as possible. This has another benefit, being that the WKZ is constantly adding ideas and requirements. This also means that the shape and behaviour of the baby is constantly changing.

The changing of the skin colour is an important aspect of the CPR doll. The skin colour is an important clue for the wellbeing of a baby. If the skin turn slightly blue the nurse must be on high alert because this can be an indication of a lack of oxygen.

## 1 – KiCad setup

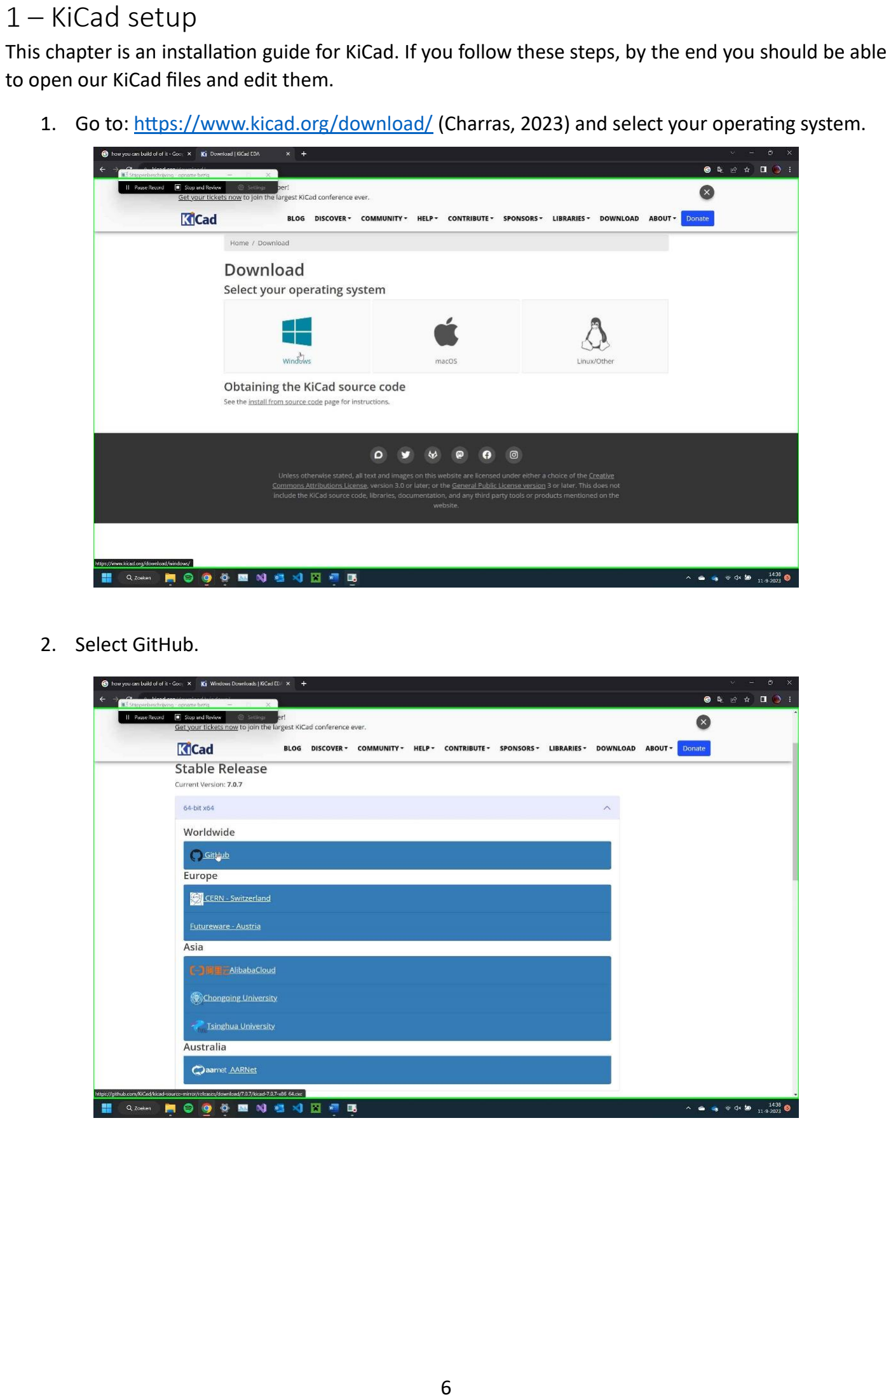
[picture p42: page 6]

This chapter is an installation guide for KiCad. If you follow these steps, by the end you should be able to open our KiCad files and edit them.

1. Go to: https://www.kicad.org/download/ (Charras, 2023) and select your operating system.
2. Select GitHub.

3. Click on the download button and select open when ready, this might take a while.
4. When downloaded, go through the installer instructions. You don’t have to do anything.
5. Congratulations, you now have access to our design files.

## 2 – Programming environment

For writing the software we can use different programming environments. In this paragraph you will find different integrated development environments (IDE) and programming methods.

### 2.1 – Visual studio code

For the setup of Visual studio code we kindly refer you to this link: https://robotpatient.github.io/Manikin_Software/General/flash_build_instructions/ (Hogeweij, Flash build instructions, 2023) a detailed description is already published here.

### 2.2 – Clion

Clion is a modern IDE made by JetBrains. You might know them from one of their other programming IDE’s or tools like: IntelliJ, PyCharm, PhpStorm or DataGrip.

In this paragraph we will show you how you can get Clion installed. How to download the required compiler and how you can start your first project.

2.2.1 – Get a JetBrains licence
If you don’t have one already go to: https://www.jetbrains.com/shop/eform/students (JetBrains, 2023) Enter the required information. Important: Use your HAN email to apply for a licence.

Follow the instructions given by JetBrains.

2.2.2 – Install Clion
After you have received your licence you now have access to a number of JetBrains products. We will only be using Clion though so head over to the JetBrains website (https://www.jetbrains.com/clion/download/#section=windows) (JetBrains, 2023):
And download Clion. Clion is available for Windows, Linux and MacOS. Run the installer as you would with any regular installer. Follow the steps in the installer.

2.2.3 – Install Arm GNU toolchain
To be able to compile and build your code you will need a platform specific toolchain. Since our microcontrollers have an ARM architecture we will need to install the ARM toolchain. Head over to the following link: https://developer.arm.com/downloads/-/arm-gnu-toolchain-downloads (ARM, 2023)

We will need the AArch32 bare-metal target (arm-none-eabi) version.

For windows: you will need the arm-gnu-toolchain-13.2.rel1-mingw-w64-i686-arm-none-eabi.exe file.

For Linux: you will need the arm-gnu-toolchain-13.2.rel1-x86_64-arm-none-eabi.tar.xz file.

For MacOS: you will need the arm-gnu-toolchain-13.2.rel1-darwin-arm64-arm-none-eabi.tar.xz file.

Run the installer. Important: make sure to check the add to path checkbox!

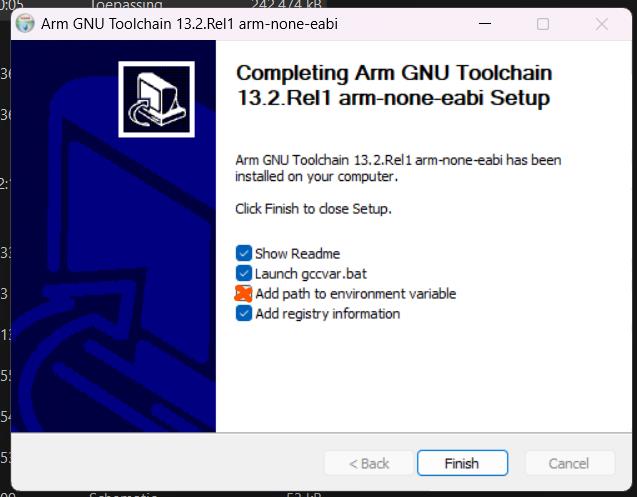
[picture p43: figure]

2.2.4 – Cloning git repository
To make it easy for you Victor Hogeweij has created a base project for us. This repository can be cloned here: https://github.com/Hoog-V/SAMD21_BARE_CMAKE (Hogeweij, samd21_bare_cmake, 2023)

If you don’t know how to clone a repository you can follow this guide: https://docs.github.com/en/repositories/creating-and-managing-repositories/cloning-a-repository (GitHub, 2023)

2.2.5 – Setting up IDE
Now we can finally startup Clion. When you first start up Clion you will see a window like this:

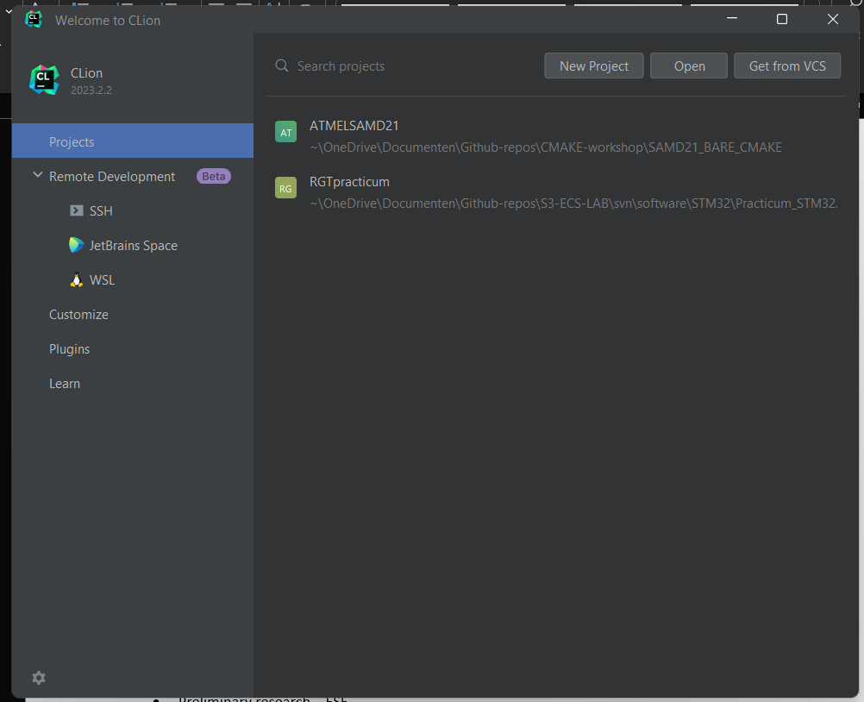
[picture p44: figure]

Go to: Open -> <browse to location of git repository> -> browse to ‘src’ -> browse to ‘CMakeList.txt’ -> click ‘OK’.

The project is now opened and will be opened when you start up Clion the next time. However we are not done yet.

2.2.6 – Setting up toolchain
We have opened a project but we cannot compile or build anything yet because we haven’t setup the compiler and debugger.

To do this, go to file -> settings -> build, execution, deployment -> toolchains

And add a new toolchain by pressing the +. Give your toolchain a name. After you’ve done that you must select the path to the GCC compiler we have just installed.

On windows you can find the installer at C:\Program Files (x86)\Arm GNU Toolchain arm-none-eabi\12.3 rel1\bin\arm-none-eabi-gcc.exe. Press ‘OK’ if you have done this.

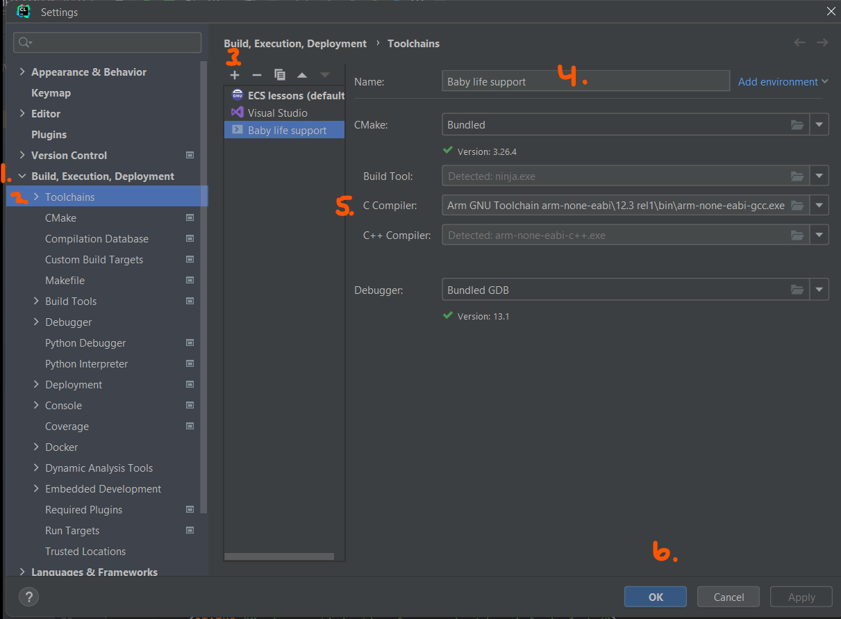
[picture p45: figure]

2.2.7 – Configuring CMake
To configure CMake go to file -> settings -> build, execution, deployment -> CMake

Add a new CMake configuration by pressing the + symbol.
Give your configuration a name.
Press ‘OK’.

Test by pressing Ctrl + F9. If you get errors about a path not being found you might want to try this next step:

Go back to the menu from before. Press the edit button in the Environment tab. A new menu will open. Press the + button once more and type PATH in the Name column. Add the path to the GCC compiler (see 2.1.6) in the Variable column. Then press OK.

Test by pressing Ctrl + F9. If there are still errors check if you’ve followed all the aforementioned steps correctly. If you still encounter problems don’t be afraid to ask for help!

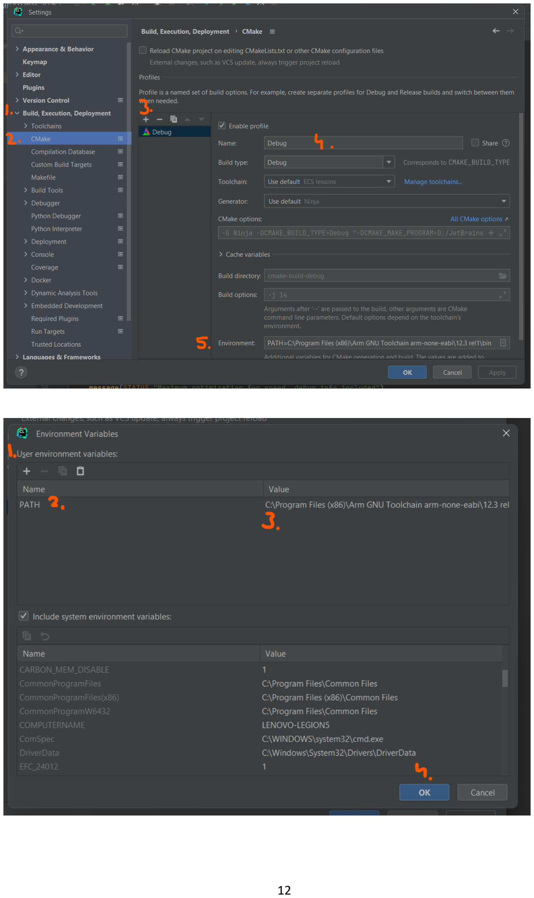
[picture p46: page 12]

### 2.3 – Flashing and debugging

Now that we have chosen an environment where we can write and compile our software in we still need to get that program onto our microcontroller board. You can do this via a couple of different ways. Here we’ll show you two ways to do this.

2.3.1 – ledDriverBoardV2:
Whether you want to install an Arduino bootloader or want to program the microcontroller using embedded C/C++ you will have to use the following method:

Plug a USB-C cable into the board. Connect the other end of the USB-C cable to a power source like a laptop. After you have done that you can connect the J-LINK EDU mini (https://www.segger.com/products/debug-probes/j-link/models/j-link-edu-mini/) (Segger, 2024) debugger to the board. The connector has a notch. The red markings in the picture below indicate where the notch should go.

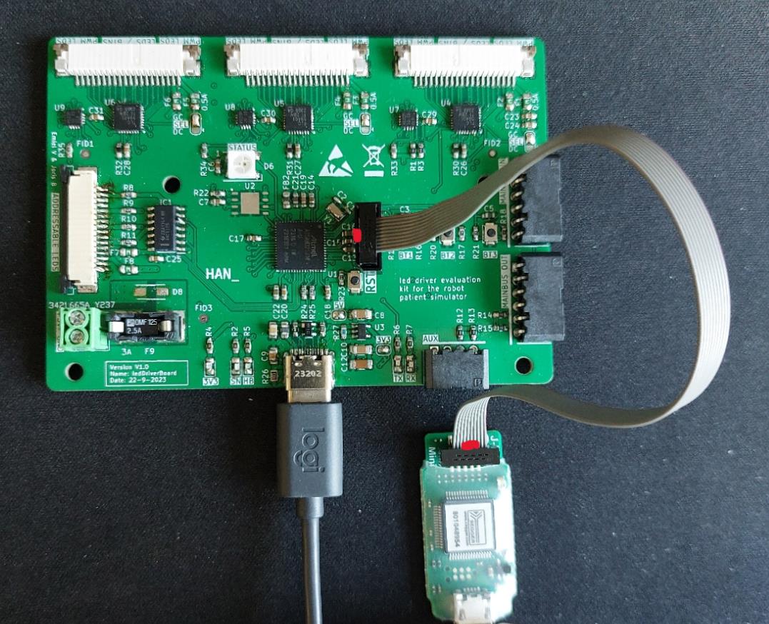
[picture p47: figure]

2.3.1.1 – Programming and debugging using Ozone:
You are now ready to upload code to the board via Clion or Visual Studio code using a program called Ozone. In Ozone the program can be started, stopped, halted and debugged.

First you will need a .jdebug project. You will find one in the code folders.

The “ON” symbol lets you connect (and flash) to a target. After that you can press the symbol next to it to start the program. In the program you will be able to step through code, see register values and set register values. Super handy.

2.3.1.2 – Uploading Arduino bootloader:
To upload the bootloader to the board we will first need to download the bootloader (https://github.com/AtmelUniversityFrance/atmel-samd21-xpro-boardmanagermodule/blob/master/module/bootloaders/atmel_samd21_xpro_v1/samd21_sam_ba.hex) (AtmelUniversityFrance, 2023). After you have done that you can open Microchip Studio -> Goto Device Programming (Ctrl + Shift + P).

A new window will open:
Tool: J-Link
Device: ATSAMD21J18A
Interface: SWD

Hit apply. Next to that section you will find the device signature and target voltage buttons. Read both of those.

Go to the fuses tab and scroll down to the USER_WORD_0.NVMCTRL_BOOTPROT fuse. Set the fuse to 0 bytes and hit program. Verify that the fuse has been set correctly.

Now you can go to the Memories tab. In the Flash section of the memories tab you have to select the bootloader you’d like to flash to the board. Hit program and wait for the message saying that the flash was successful.

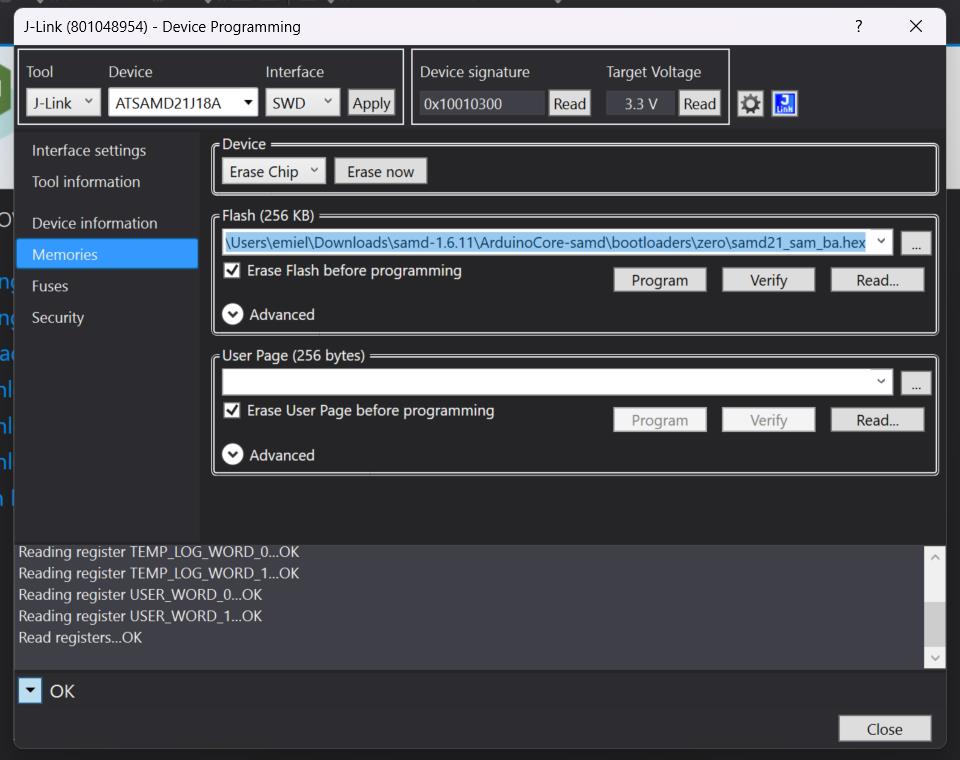
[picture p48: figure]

However we are not done yet. We still have to set the bootprot fuse back to 8192 bytes otherwise the bootloader will be overwritten when we flash our code to the board. Don’t forget to hit program again after setting the fuse!

2.3.2 – LedDriverBoardV3:
Whether you want to install an Arduino bootloader or want to program the microcontroller using embedded C(++) you will have to use the following method:

Plug a USB-C cable into the board. Connect the other end of the USB-C cable to a power source like a laptop. After you have done that you can connect the J-LINK EDU mini (https://www.segger.com/products/debug-probes/j-link/models/j-link-edu-mini/) (Segger, 2024) debugger to the board. Because we didn’t connect the debug header correctly you will have to use the solder pads on the back of the board to access the debug interface.

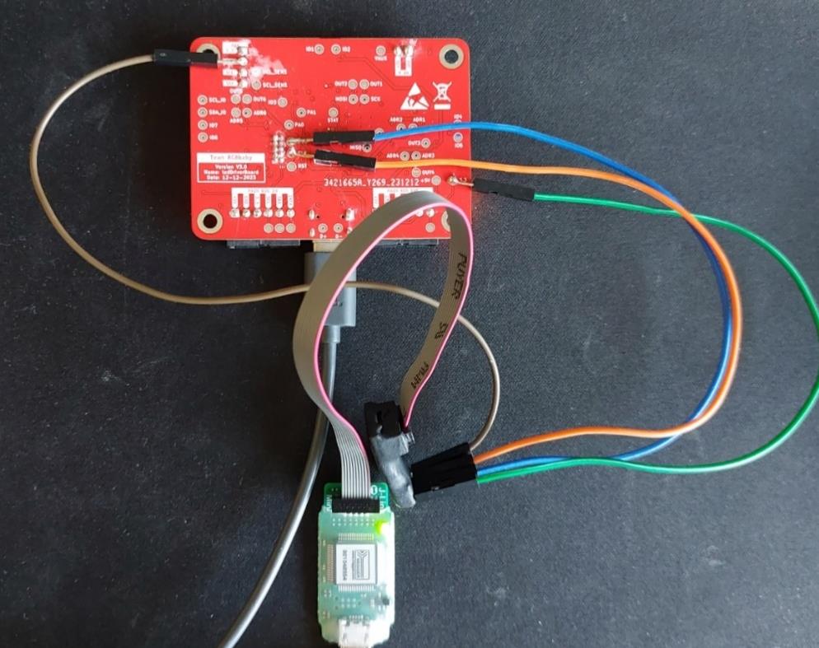
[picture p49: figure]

2.3.2.1 – Programming and debugging using Ozone:
You are now ready to upload code to the board via Clion or Visual Studio code using a program called Ozone. In Ozone the program can be started, stopped, halted and debugged.

First you will need a .jdebug project. You will find one in the code folders.

The “ON” symbol lets you connect (and flash) to a target. After that you can press the symbol next to it to start the program. In the program you will be able to step through code, see register values and set register values. Super handy.

2.3.2.2 – Uploading Arduino bootloader:
To upload the bootloader to the board we will first need to download the bootloader (https://github.com/adafruit/uf2-samdx1/releases/download/v3.15.0/bootloader-feather_m0_express-v3.15.0.bin) (Adafruit, 2023) After you have done that you can open Microchip Studio -> Goto Device Programming (Ctrl + Shift + P).

A new window will open:
Tool: J-Link
Device: ATSAMD21JG8A
Interface: SWD

Hit apply. Next to that section you will find the device signature and target voltage buttons. Read both of those.

Go to the fuses tab and scroll down to the USER_WORD_0.NVMCTRL_BOOTPROT fuse. Set the fuse to 0 bytes and hit program. Verify that the fuse has been set correctly.

Now you can go to the Memories tab. In the Flash section of the memories tab you have to select the bootloader you’d like to flash to the board. Hit program and wait for the message saying that the flash was successful.

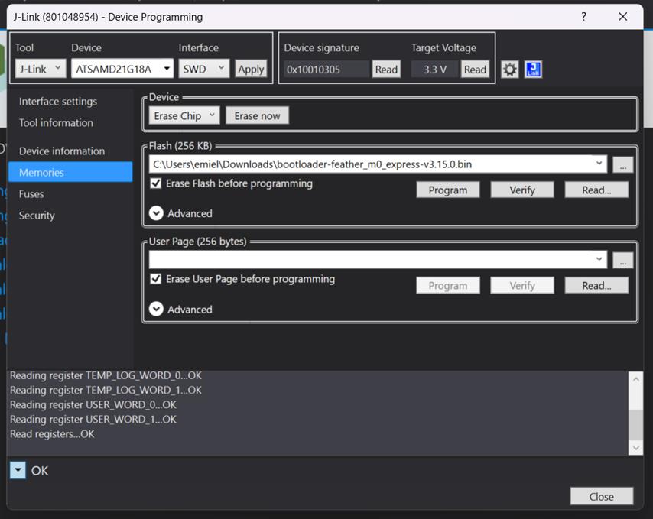
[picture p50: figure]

However we are not done yet. We still have to set the bootprot fuse back to 8192 bytes otherwise the bootloader will be overwritten when we flash our code to the board. Don’t forget to hit program again after setting the fuse!

## 3 – Hardware

In this chapter we will describe how you can use the PCBs we have made.

### 3.1 – LedDriverBoardV2

The second version (V1.0 on the
silkscreen, this is a mistake) of our
PCB is a test bed for a couple of different methods we wanted to try to drive the LEDs we wanted to test.

3.1.1 – Power:
You can power this board by inserting a USB-C cable in the USB port. The USB port can output
5V@3A max.

We also included the possibility to

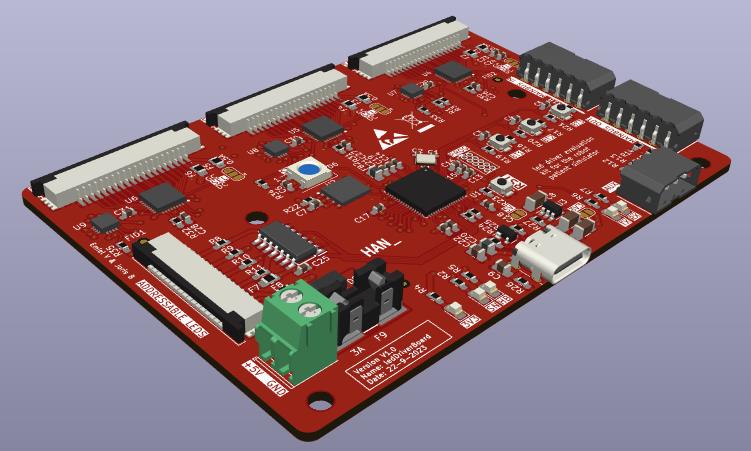
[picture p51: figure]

use an external power supply (green connector). The supply voltage is 5V max. The fuse in the fuse holder is a replaceable 2.5A fast blow fuse.

The default way of powering the system is by using the main communication bus. The connectors for the main bus are the two black 6pin connectors on our board.

3.1.2 – First power up:
Assuming that you have installed the bootloader on the chip we can now connect our USB-C cable or debugger to the board. The device should register as a COM port on your windows device. If you’re using a debugger you have to manually connect to it using the firmware your debugger uses.

3.1.3 – Programming:
You can use your preferred IDE to program our board. For the test code we have used Arduino. However, we recommend programming on register level due to some limitations with our design. More on that later.

3.1.4 – Inputs:
There are several inputs available on our board. We have broken out three user addressable buttons which can be used for all sorts of applications. The main bus in and main bus out ports both have an interrupt enabled pin.

3.1.5 – Busses:
We have three I2C busses on out board. The main system bus. This bus is used to communicate with other modules. We have an auxiliary bus. This bus is used for auxiliary I2C sensors or actuators. And lastly, we have an IO I2C bus. This bus is connected to the IO multiplexers. The FRAM-chip is connected via QSPI to the microcontroller. You can use this chip to store data. It has a storage capacity of 64 kB.

Note: Due to time limitations and problems with the hardware of our PCB we have not been able to get these busses to function on this board.

3.1.6 – Outputs:
This board has several output possibilities. Most of them control LEDs. The led drivers are driven with a dedicated communication protocol. You can find more information about this protocol in the manufactures datasheet (https://www.ti.com/lit/ds/symlink/tlc59401.pdf?ts=1704793969761) (Texas Instruments, 2023). The onboard neopixel is connected to the standard neopixel pin on for example a Adafruit Feather M0 Express. The addressable led strip works via the same principle as the onboard neopixel.

There are several status LEDs on our board. The 3.3V led is not addressable by the user and powers on when the 3.3V LDO (voltage regulator) is supplied with 5V.

3.1.7 – Jumper selections:
There are a bunch of jumpers on this board. In this section we will explain their function. The jumpers marked in red are the mode selection jumpers for the PWM drivers. Currently they have been set to normal mode. The other option is running them in grayscale mode. For more information about these modes. Please refer to the datasheet (https://www.ti.com/lit/ds/symlink/tlc59401.pdf?ts=1704793969761) (Texas Instruments, 2023).

The jumper marked in blue with the 3V3 tag above it connects the LDO (3.3V regulator) to the 3.3V net on the PCB. This jumper must be bridged if no other 3.3V supply is connected. Otherwise the PCB won’t do anything.

The other jumper marked in blue with the 5V tag above it connects VBUS (5V from USB port) to the 5V net on the PCB. This jumper can be left open if a 5V supply is attached to the PCB.

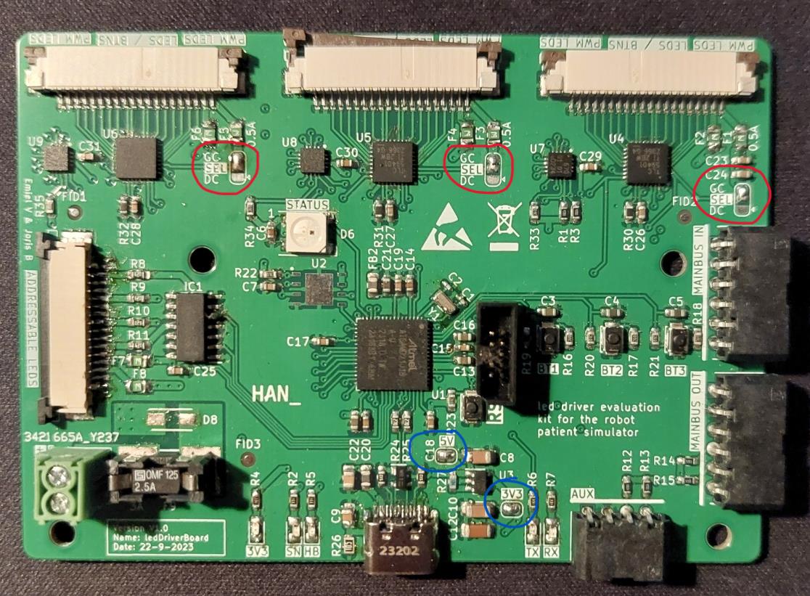
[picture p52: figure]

3.1.8 – Problems:
We had a bunch of problems with this board. Mainly finding a suitable Arduino bootloader and libraries for the IO expanders, FRAM chip and led drivers. This is why we recommend programming on register level. We didn’t have time for this however so we settled on Arduino for our tests.

3.1.9 – Things to lookout for:
Each led power rail (5V and 3.3V) each have their own 0.5A polyfuse. The maximum allowed current via the external power port is 2.5A. This means this fuse will blow if all led channels are ran at their maximum rating.

The USB and main bus port don’t have fuses though. So make sure you don’t pull more than 3A through those connectors.

### 3.2 – FlexledsV1.0

This flexible PCB
has a couple of
different LEDs
we wanted to
test on it. This is
also the PCB that
has two types of
buttons on it.
This PCB can
only be used

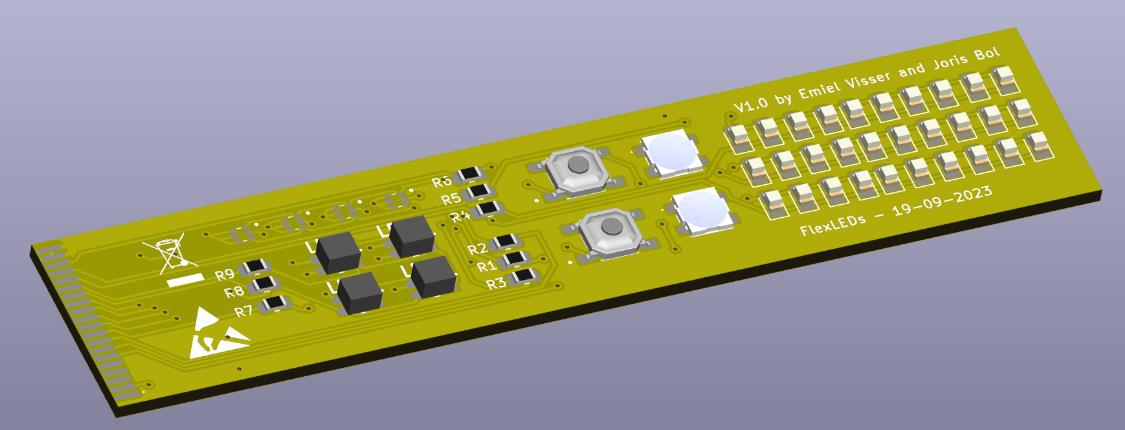
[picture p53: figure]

with the 20pin FPC connector and must be inserted with the components facing up. We have not been able to test this PCB because of the aforementioned issues we ran into with the LedDriverBoardV2.

3.2.1 – Connecting the flex PCB:
To connect the flex PCB to the main PCB you must first disconnect any power sources connected to the ledDriverBoard. After you have verified that the board is in an unpowered state you can start by pulling the locking tab of one of the 20pin FFC connectors out. The tabs are made out of plastic and break easily if you pull too hard on them. So don’t be too rough with them.

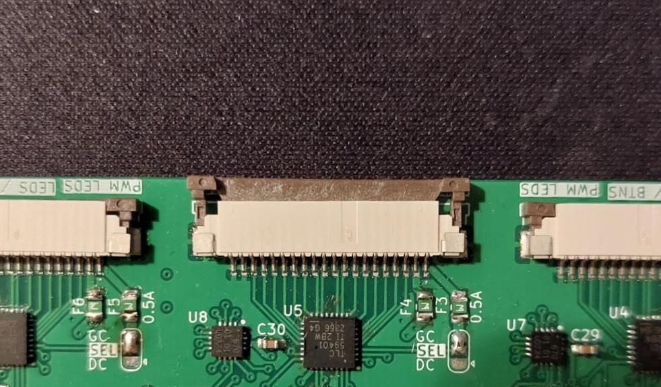
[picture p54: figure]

After you have done that you can push the flex PCB, components facing up, in the connector. Make sure the flex PCB is pushed all the way in and is not going in at an angle. This could cause shorts.

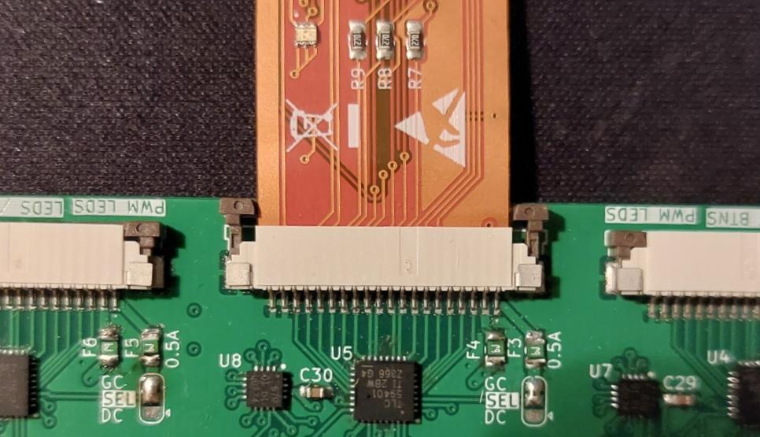
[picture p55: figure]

Now you can push in the locking tab. It won’t lock all the way down because the flex PCB is bit too thick for the connector. Just push it in until the PCB feels snug. It should look something like this:

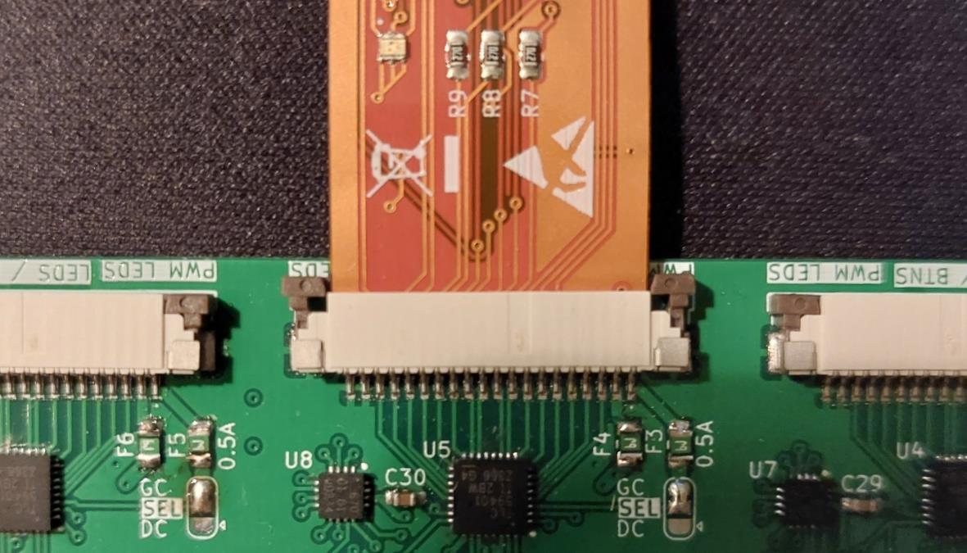
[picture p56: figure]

### 3.3 – flexAddresLedsV1.0

This flexible PCB has
the addressable LEDs
on it. This PCB has o
buttons | or | other
inputs | on | it | in
contrary | to | the
flexLedsV1.0 PCB we
saw earlier. This flex
PCB | is | | only
compatible with the
16pin FPC connector.
The PCB must be

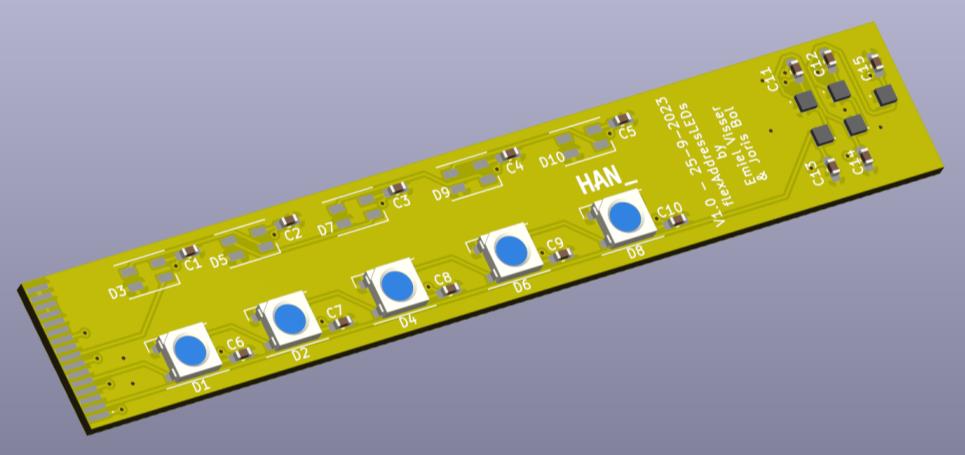
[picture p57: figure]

inserted with the components facing up. This board is fully operational.

3.3.1 – Connecting the flex PCB:
To connect the flex PCB to the main PCB main PCB you must first disconnect any power sources connected to the ledDriverBoard. After you have verified that the board is in an unpowered state you can start by pulling the locking tab of the 16pin FFC connector out.

Note: If you’ve soldered a new PCB you will have to pull out the plastic tab completely and flip it around 180 degrees. Otherwise the pins in the connector won’t make contact with the pads on the flex PCB.

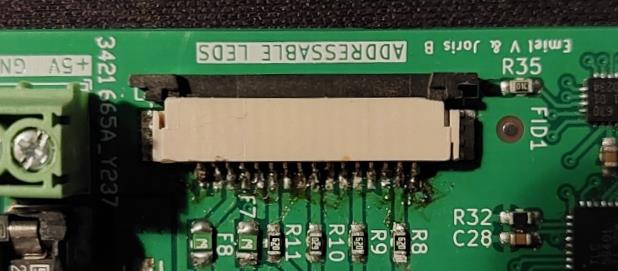
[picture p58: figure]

You can now pull the locking tab out carefully. It’s easy to pull the tab out completely because the plastic piece locking it in has been broken off.

After you have done that you can push the flex PCB, components facing up, in the connector. Make sure the flex PCB still has a small part of the contact points visible. So don’t push it in all the way this time. Make sure the PCB is going in straight and is not going in at an angle. This could cause shorts!

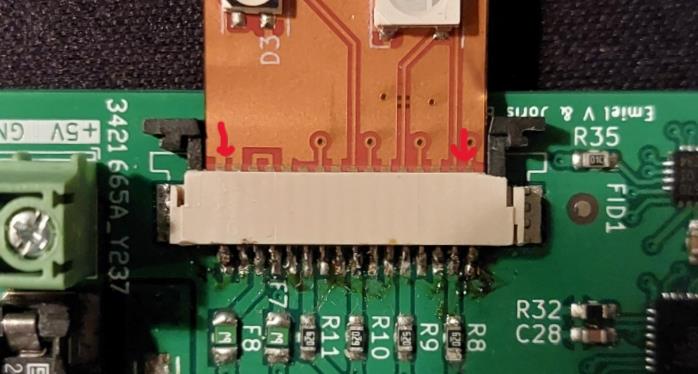
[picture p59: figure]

Now you can carefully push in the locking tab. It’s easier to do this one side at a time and adjust the flex PCB as needed because the flex PCB tends to go in crooked if you push in both sides of the tab at the same time. Pushing in one side at a time enables you to adjust the orientation of the PCB before it is locked in completely.

### 3.4 – LedDriverBoardV3

The third version of our PCB is our final version. We decided to drop the PWM drivers and IO expanders and choose to go with addressable LEDs.

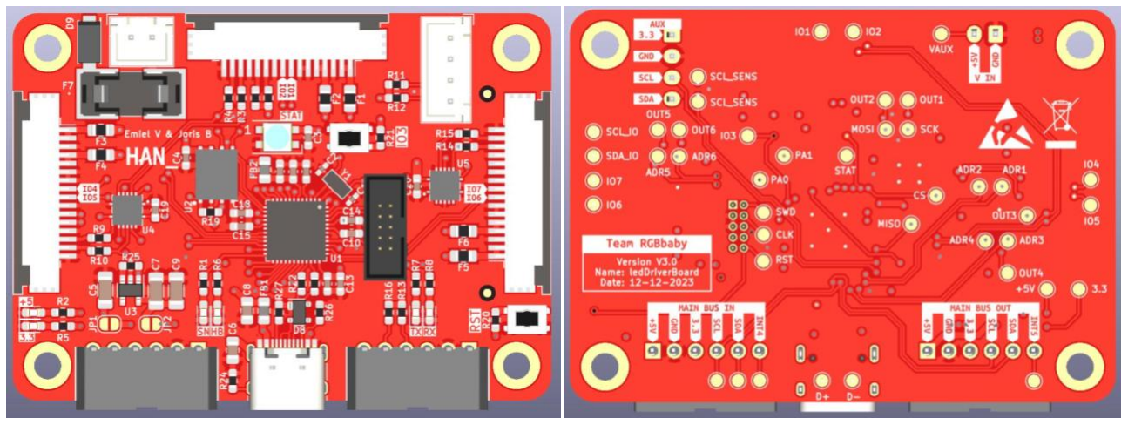
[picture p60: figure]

3.4.1 – Power:
You can power this board by inserting a USB-C cable in the USB port. The USB port can output 5V@3A max.

We also included the possibility to use an external power supply (2pin JST connector). The supply voltage is 5V max. The fuse in the fuse holder is a replaceable 3A fast blow fuse.

The default way of powering the system is by using the main communication bus. The connectors for the main bus are the two black 6pin connectors.

3.4.2 – First power up:
Assuming that you have installed the bootloader on the chip we can now connect our USB-C cable or debugger to the board. The device should register as a COM port on your windows device. If you’re using a debugger you have to manually connect to it using the firmware your debugger uses.

3.4.3 – Programming:
You can use your preferred IDE to program our board. For the test code we have used Arduino. However, we recommend programming on register level because this gives you more flexibility and reliability.

3.4.4 – Inputs:
There are several inputs available on our board. We have broken out one user addressable button which can be used for all sorts of applications. The main bus in and main bus out ports both have an interrupt enabled pin. We also have connected two IO pins to each of the three FFC connectors.

3.4.5 – Busses:
We have three I2C busses on out board. The main system bus. This bus is used to communicate with other modules. We have an auxiliary bus. This bus is used for auxiliary I2C sensors or actuators. And lastly, we have an IO I2C bus. This bus is connected to 16pin FFC connectors and can be used to connect I2C devices that are on the flex PCBs. The FRAM-chip is connected via QSPI to the microcontroller. You can use this chip to store data. It has a storage capacity of 64 kB.

Note: Due to time constraints we have not been able to get these busses to function on this board.

3.4.6 – Outputs:
This board has several output possibilities. Most of them control LEDs. The onboard neopixel is connected to the standard neopixel pin on for example a Adafruit Feather M0 Express. The addressable led strips works via the same principle as the onboard neopixel.

There are several status LEDs on our board. The 5V and 3.3V LEDs are not addressable by the user and power on when 5V is applied and when the 3.3V LDO (voltage regulator) is supplied with 5V.

3.4.7 – Jumper selections:
There are a bunch of jumpers on this board. In this section we will explain their function.

The jumper marked in green connects the LDO (3.3V regulator) to the 3.3V net on the PCB. This jumper must be bridged if no other 3.3V supply is connected. Otherwise the PCB won’t do anything.

The other jumper marked in blue connects VBUS (5V from USB port) to the 5V net on the PCB. This jumper can be left open if a 5V supply is attached to the PCB.

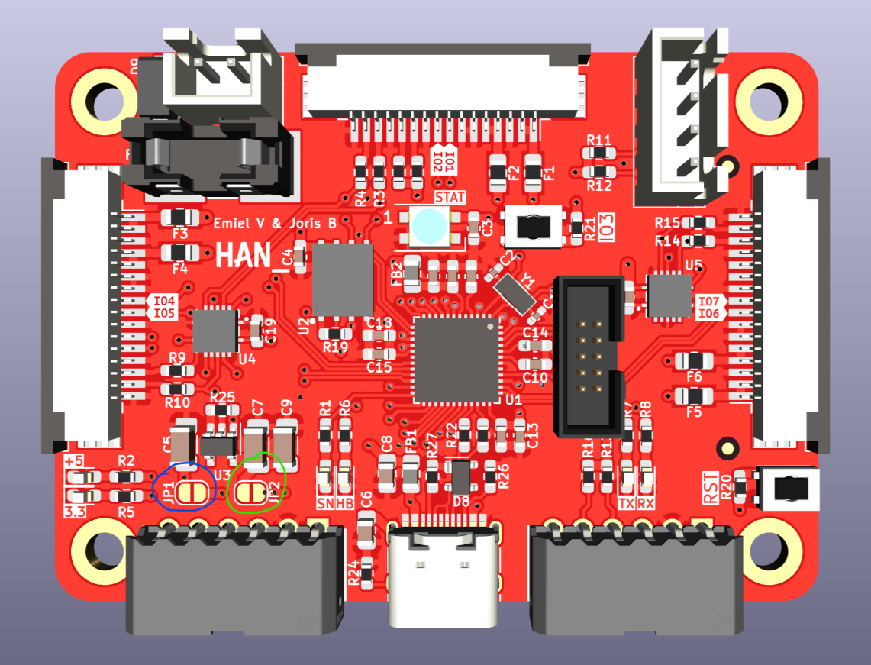
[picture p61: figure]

3.4.8 – Problems:
The debug header is incorrectly connected. You must use the 3.3V, GND, SWD and CLK pads on the bottom side of the board.

3.4.9 – Things to lookout for:
Each led power rail (5v and 3.3V) each have their own 1A polyfuse. The maximum allowed current via the external power port is 3A. This means this fuse will blow if all led channels are ran at their maximum rating.

The USB and main bus port don’t have fuses though. So make sure you don’t pull more than 3A through those connectors.

### 3.5 – flexAddressLedsV2.3

This flexible PCB has a
couple of different LEDs
we wanted to test on it.
This is also the PCB that
has two types of buttons
on it. This PCB can only
be used with the 20pin
FPC connector and must
be inserted with the
components facing up.
We have not been able to
test this PCB because of
the aforementioned
issues we ran into with
the LedDriverBoardV2.

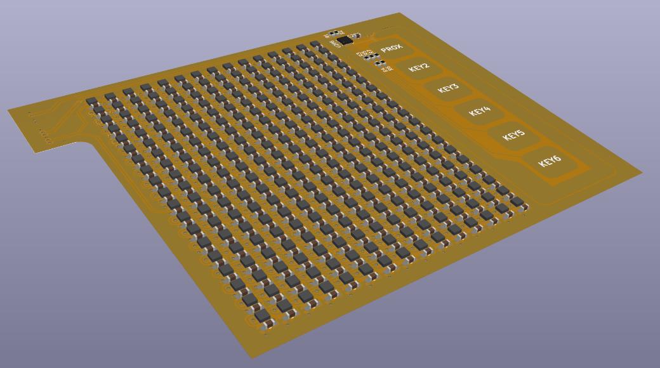
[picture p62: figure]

3.5.1 – Connecting the flex PCB:
To connect the flex PCB to the main PCB you must first disconnect any power sources connected to the ledDriverBoard. After you have verified that the board is in an unpowered state you can start by pulling the locking tab of one of the 20pin FFC connectors out. The tabs are made out of plastic and break easily if you pull too hard on them. So don’t be too rough with them.

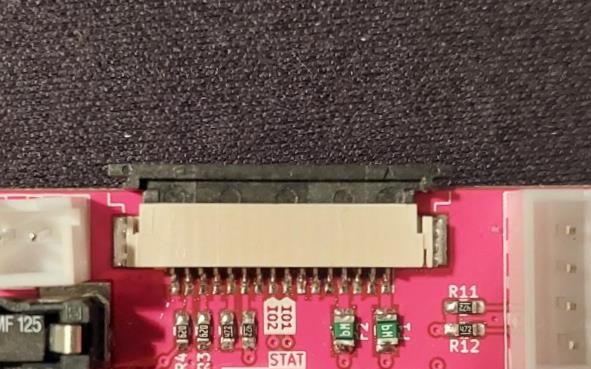
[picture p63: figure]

After you have done that you can push the flex PCB, components facing up, in the connector. Make sure the flex PCB is pushed all the way in and is not going in at an angle. This could cause shorts.

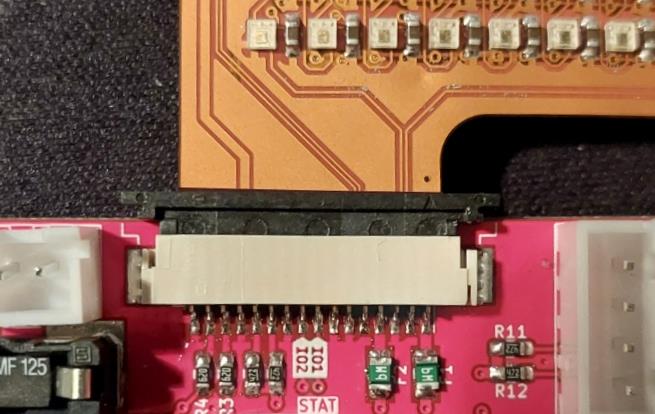
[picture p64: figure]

Now you can push in the locking tab. It won’t lock all the way down because the flex PCB is bit too thick for the connector. Just push it in until the PCB feels snug. It should look something like this:

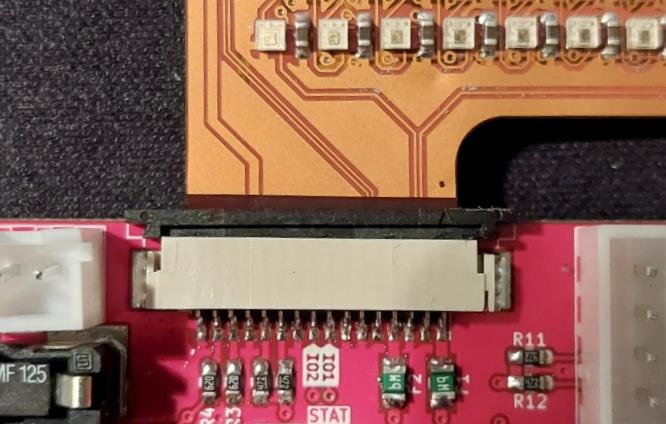
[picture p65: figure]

## 4 – Testing setup

This chapter is about the way we tested certain aspects of our product. This includes unit testing but also the spectrometer setup.

### 4.1 – PySpectrometer

If you want to recreate the experiments mentioned in the product rapport, you will need the following hardware:

- | PicCamera | (provided)
- | Spectrometer | (provided)
- | RICOH HF16HL-1b | (provided by school)
- Raspberry Pi 4 or higher

This spectrometer project is made by leswright1977. The full documentation can be found at: https://github.com/leswright1977/PySpectrometer2 (Wright, 2023)

Keep in mind that this tutorial is based on the 2022 release.

4.1.1 – Initial setup
You will need a 16GB or more SD-card that fits in your Raspberry Pi. You need to put the latest release of the Raspberry Pi Operating System (OS) on the drive. Its recommend that you use the Raspberry Pi imager to do this. The imager can be downloaded from here that can be downloaded here: https://www.raspberrypi.com/software/ (Raspberrypi foundation, 2023)

After you put the SD-card in the Raspberry Pi, you are now ready to connect the Pi to the internet. This can most easily be done with an ethernet cable.

Make sure your computer is also connected to the same network as your Pi and open the command prompt (CMD). you can now connect to your Raspberry Pi by entering:

C:\Users\name> ssh <host name> | (the host name is just the name of your pi)

C:\Users\name> <host name> password: <your password>

If everything went correctly, you should see this in your CMD:

<host name>@raspberrypi:~ $

4.1.2 – Installing the necessary software
We need to install the following software:
- | git | (this tutorial assumes that you already have git installed)
- python3-opencv

We will start by cloning the repository from GitHub.

<host name>@raspberrypi:~ $ cd Documents

<host | name>@raspberrypi:~ | /Documents | $ | git | clone
https://github.com/leswright1977/PySpectrometer2.git

Next we will install opencv:

<host name>@raspberrypi:~ $ cd

<host name>@raspberrypi:~ $ sudo apt-get install python3-opencv

4.1.3 – Running the program
<host name>@raspberrypi:~ $ cd Documents/PySpectrometer2/src

<host name>@raspberrypi:~ /Documents/PySpectrometer2/src $ chmod +x PySpectrometer2-Pycam2-v1.0.py

<host | name>@raspberrypi:~ | /Documents/PySpectrometer2/src | $
./PySpectrometer2-Pycam-v1.0.py

To see what the program does, you need to connect a monitor to the pi or use VNC Viewer.

It is important that you connect the camera to your pi first before running the program, otherwise the program will NOT run.

4.1.4 – Hardware
The test setup parts should be provided to you, if not, you can 3D print them yourself with the files we made for you. Assemble the parts and run the program.

## 5 – Documents and documentation method

This chapter describes where we documented certain topics and how we worked. Our research produced the following documents:

- Plan of Approach.
- Preliminary research – ESE.
- Preliminary research – IPO.
- Product report.
- This document.

Plan of approach
This document is one of lesser importance for you, although we do recommend you make one yourself. This document contains the semester planning and other organizational information, specific to us.

Preliminary research – ESE
If you want to find out more about why we made certain choices regarding component selection, this is the place to be. It talks about why we chose the led that we did and why we selected the pressure sensor we use.

Preliminary research – IPO
This is one of the more important and interesting reports regarding the creation of the skin. Noted is the selection of the silicone and pigments used as well as the research regarding the thickness and colour of the skin.

Product report
This is the main report, containing all the technical details and the project process. Important chapters in this report are:
- Functional design:
You can find to what and goal we worked end what the starting conditions of this project were.
- Technical design:
Here all the technical requirements can be found, some are mandatory, made by the product owner and some are made by us.
- Realisation:
In this chapter you can find how we developed the actuator as well as the skin. If you are wondering how we did something or why regarding the actual construction of our product, this is the place to look.

This document
For more information about this document, we kindly refer you to the preface on page 4.

## 6 – Bibliography

Adafruit. (2023). v3.15.0. Retrieved from github: https://github.com/adafruit/uf2-samdx1/releases/download/v3.15.0/bootloader-feather_m0_express-v3.15.0.bin

ARM. (2023). arm gnu toolchain downloads. Retrieved from developer.arm.com: https://developer.arm.com/downloads/-/arm-gnu-toolchain-downloads

AtmelUniversityFrance. (2023). atmel_samd21_xpro_v1. Retrieved from github: https://github.com/AtmelUniversityFrance/atmel-samd21-xpro-boardmanagermodule/blob/master/module/bootloaders/atmel_samd21_xpro_v1/samd21_sam_ba.hex

Charras, J.-P. (2023). KiCad download page. Retrieved from kicad.org: https://www.kicad.org/download/

GitHub. (2023). cloning a repository. Retrieved from docs.github.com: https://docs.github.com/en/repositories/creating-and-managing-repositories/cloning-a-repository

Hogeweij, V. (2023). Flash build instructions. Retrieved from GitHub: https://robotpatient.github.io/Manikin_Software/General/flash_build_instructions/

Hogeweij, V. (2023). samd21_bare_cmake. Retrieved from github: https://github.com/Hoog-V/SAMD21_BARE_CMAKE

JetBrains. (2023). clion. Retrieved from jetbrains: https://www.jetbrains.com/clion/download/#section=windows

JetBrains. (2023). students. Retrieved from jetbrains: https://www.jetbrains.com/shop/eform/students

Raspberrypi foundation. (2023). software. Retrieved from raspberrypi: https://www.raspberrypi.com/software/

Segger. (2024). j-link-edu-mini. Retrieved from segger: https://www.segger.com/products/debug-probes/j-link/models/j-link-edu-mini/

Texas Instruments. (2023). 16-channel led driver with dot correction and grayscale pwm control. Retrieved from TI:
https://www.ti.com/lit/ds/symlink/tlc59401.pdf?ts=1704793969761&ref_url=https%253A%2 52F%252Fwww.ti.com%252Fproduct%252FTLC59401

Wright, L. (2023). PySpectrometerV2. Retrieved from github: https://github.com/leswright1977/PySpectrometer2

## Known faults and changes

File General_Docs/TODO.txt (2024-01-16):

TODO 16-1-2024: 
	- Fix short on flexPCB.
	- Fix clock issue on main PCB.
	- Finish code so PCBs can be tested.
	- Inplement solution in baby. (might require the creation of a new flexible PCB).
	
To finish the code you will be missing som files:
	- Add this repo https://github.com/evanic14/SAMD21_BARE_CMAKE to this file path LedDriverBoardV2/Code/SAMD21_BARE_CMAKE
	- Add this repo https://github.com/janelia-arduino/AT42QT to this file path PCBs/LedDriverBoardV3/Code/clio-platformio/.pio/libdeps/adafruit_feather_m0_express/AT42QT/
	- Add this repo https://github.com/RobotPatient/FreeRTOS to this file path PCBs/LedDriverBoardV3/Code/clio-platformio/.pio/libdeps/adafruit_feather_m0_express/FreeRTOS_SAMD21/

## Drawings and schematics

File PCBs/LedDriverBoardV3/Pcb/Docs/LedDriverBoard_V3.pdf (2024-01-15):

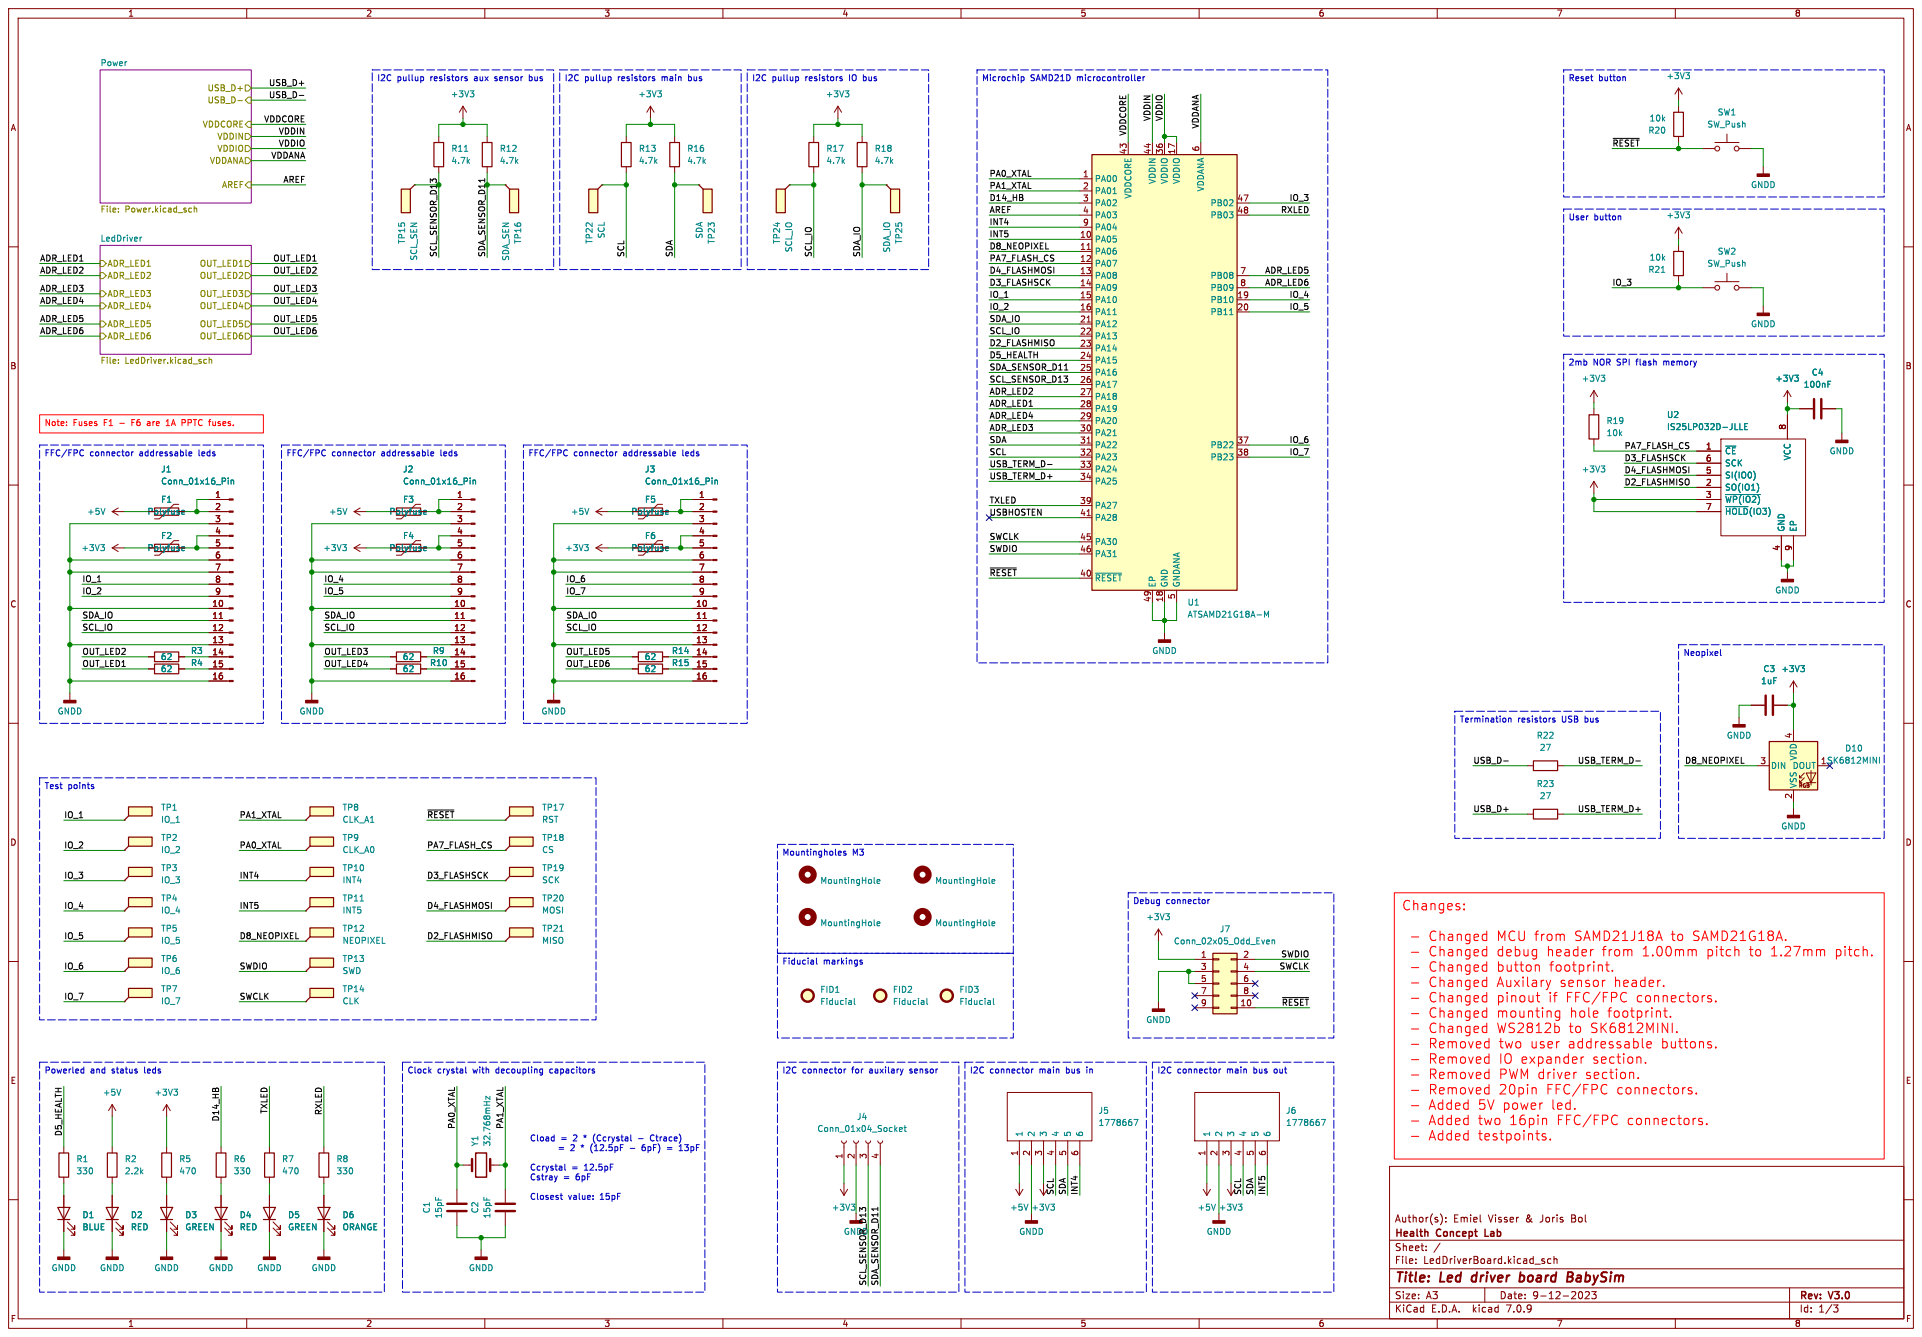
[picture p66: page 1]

LedDriver File: LedDriver.kicad_sch VDDANA

2mb NOR SPI flash memory

9 ~{CE} 1 SO(IO1) 2 ~{WP(IO2)} 3 SI(IO0) 5 ~{HOLD}(IO3) 7 U2
IS25LP032D-JLLE

9 ~{CE} 1 SO(IO1) 2 ~{WP(IO2)} 3 SI(IO0) 5 ~{HOLD}(IO3) 7

Cstray = 6pF Closest value: 15pF Powerled and status leds

Id: 1/3 Title: Led driver board BabySim

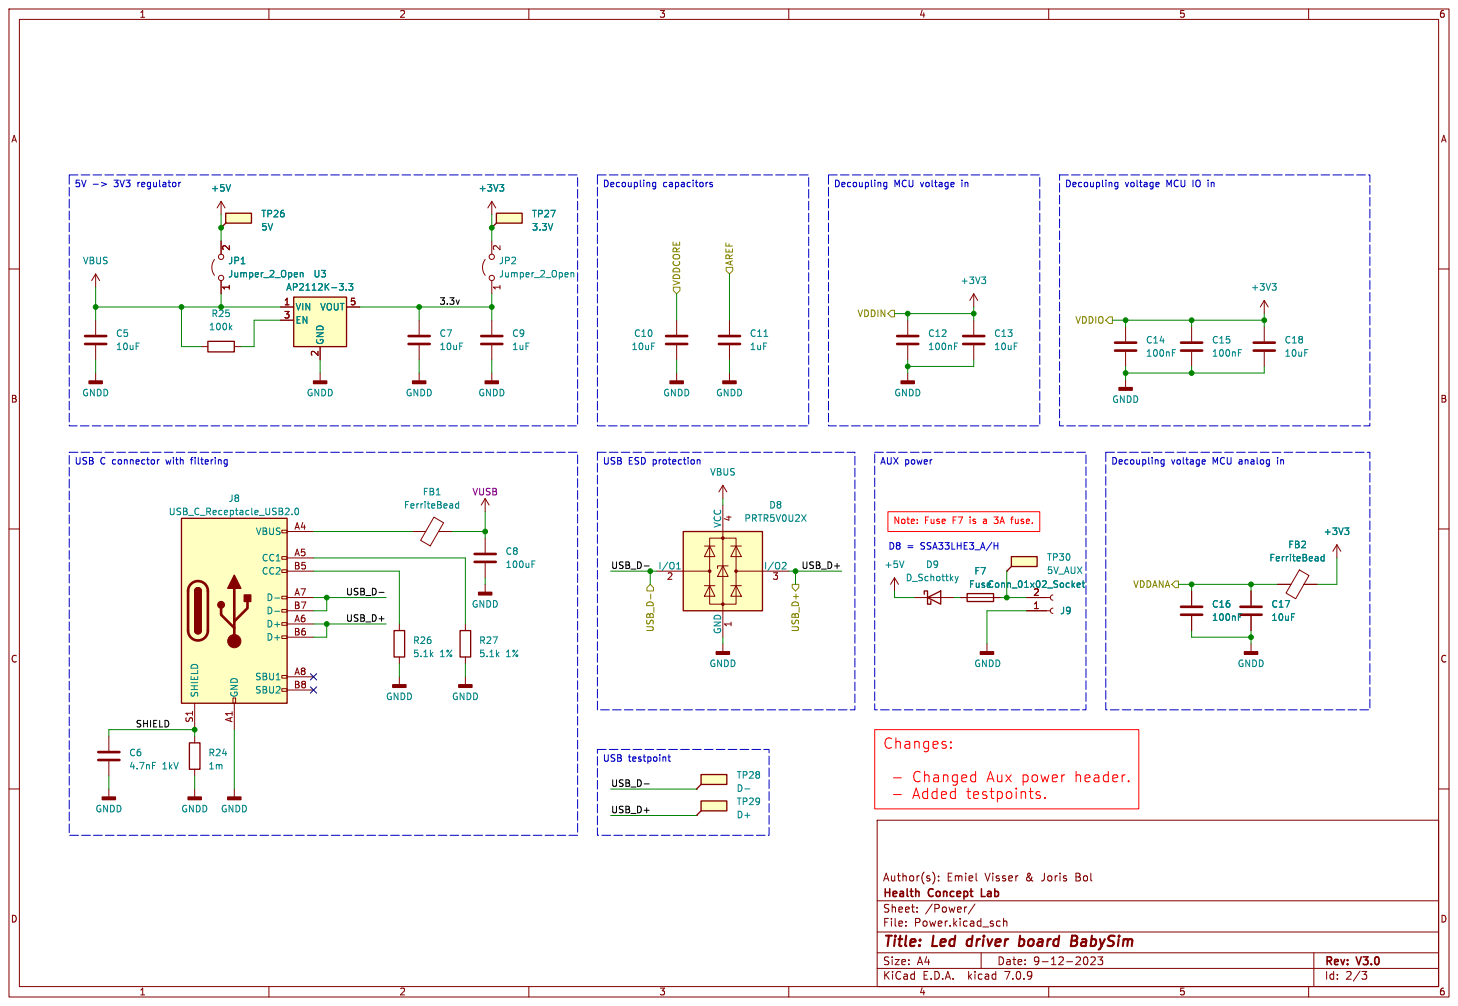
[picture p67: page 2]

Id: 2/3 Title: Led driver board BabySim

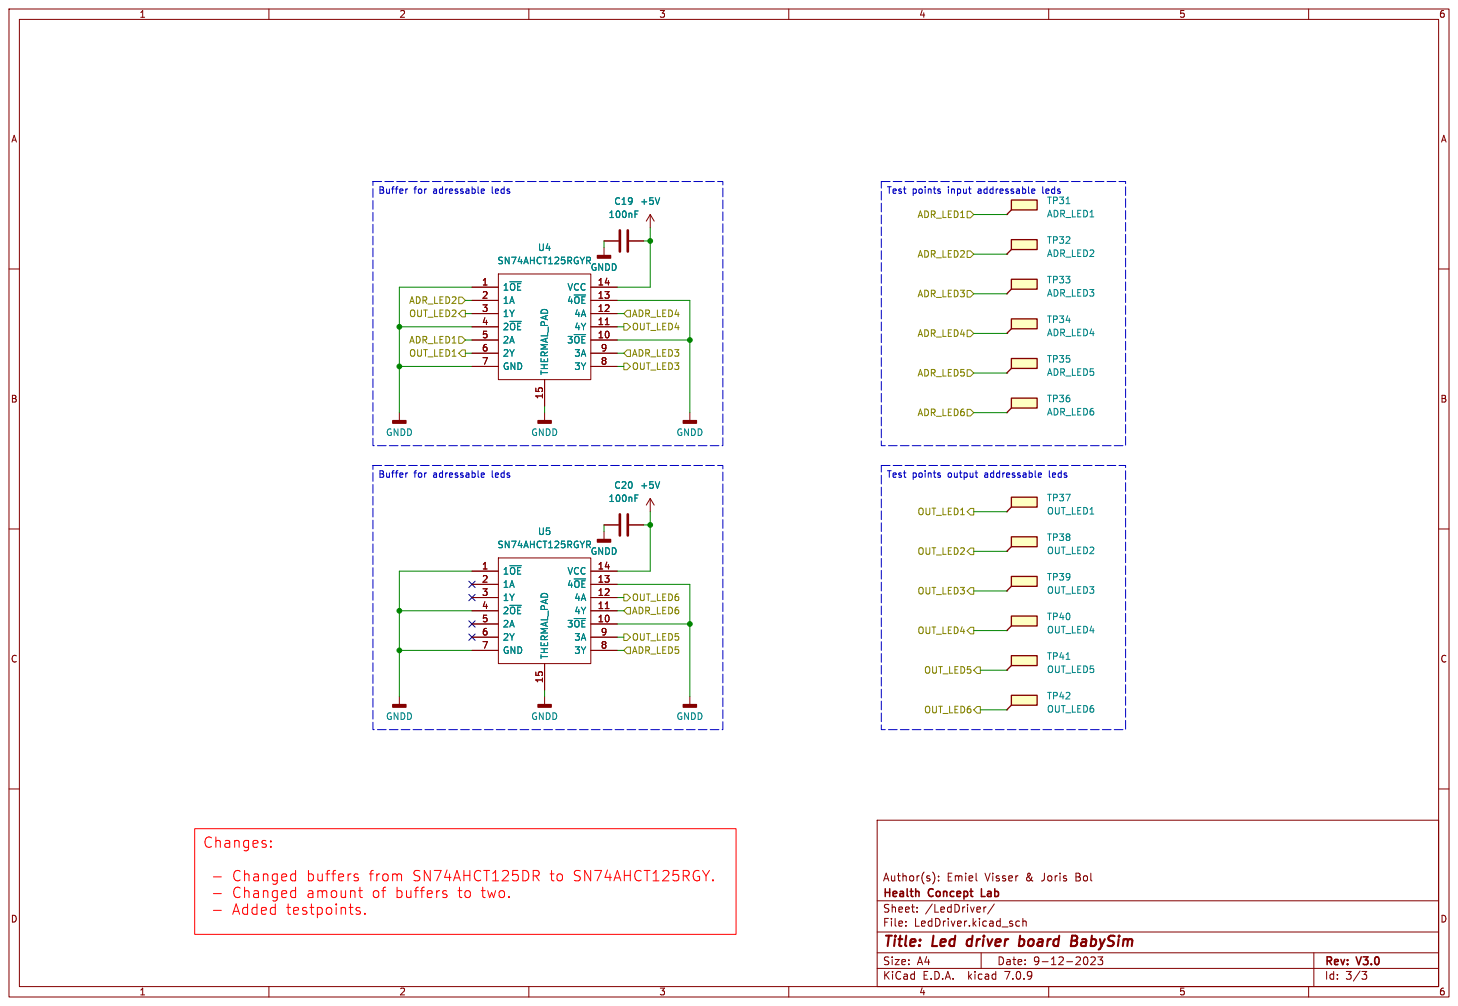
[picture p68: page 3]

Id: 3/3 Title: Led driver board BabySim

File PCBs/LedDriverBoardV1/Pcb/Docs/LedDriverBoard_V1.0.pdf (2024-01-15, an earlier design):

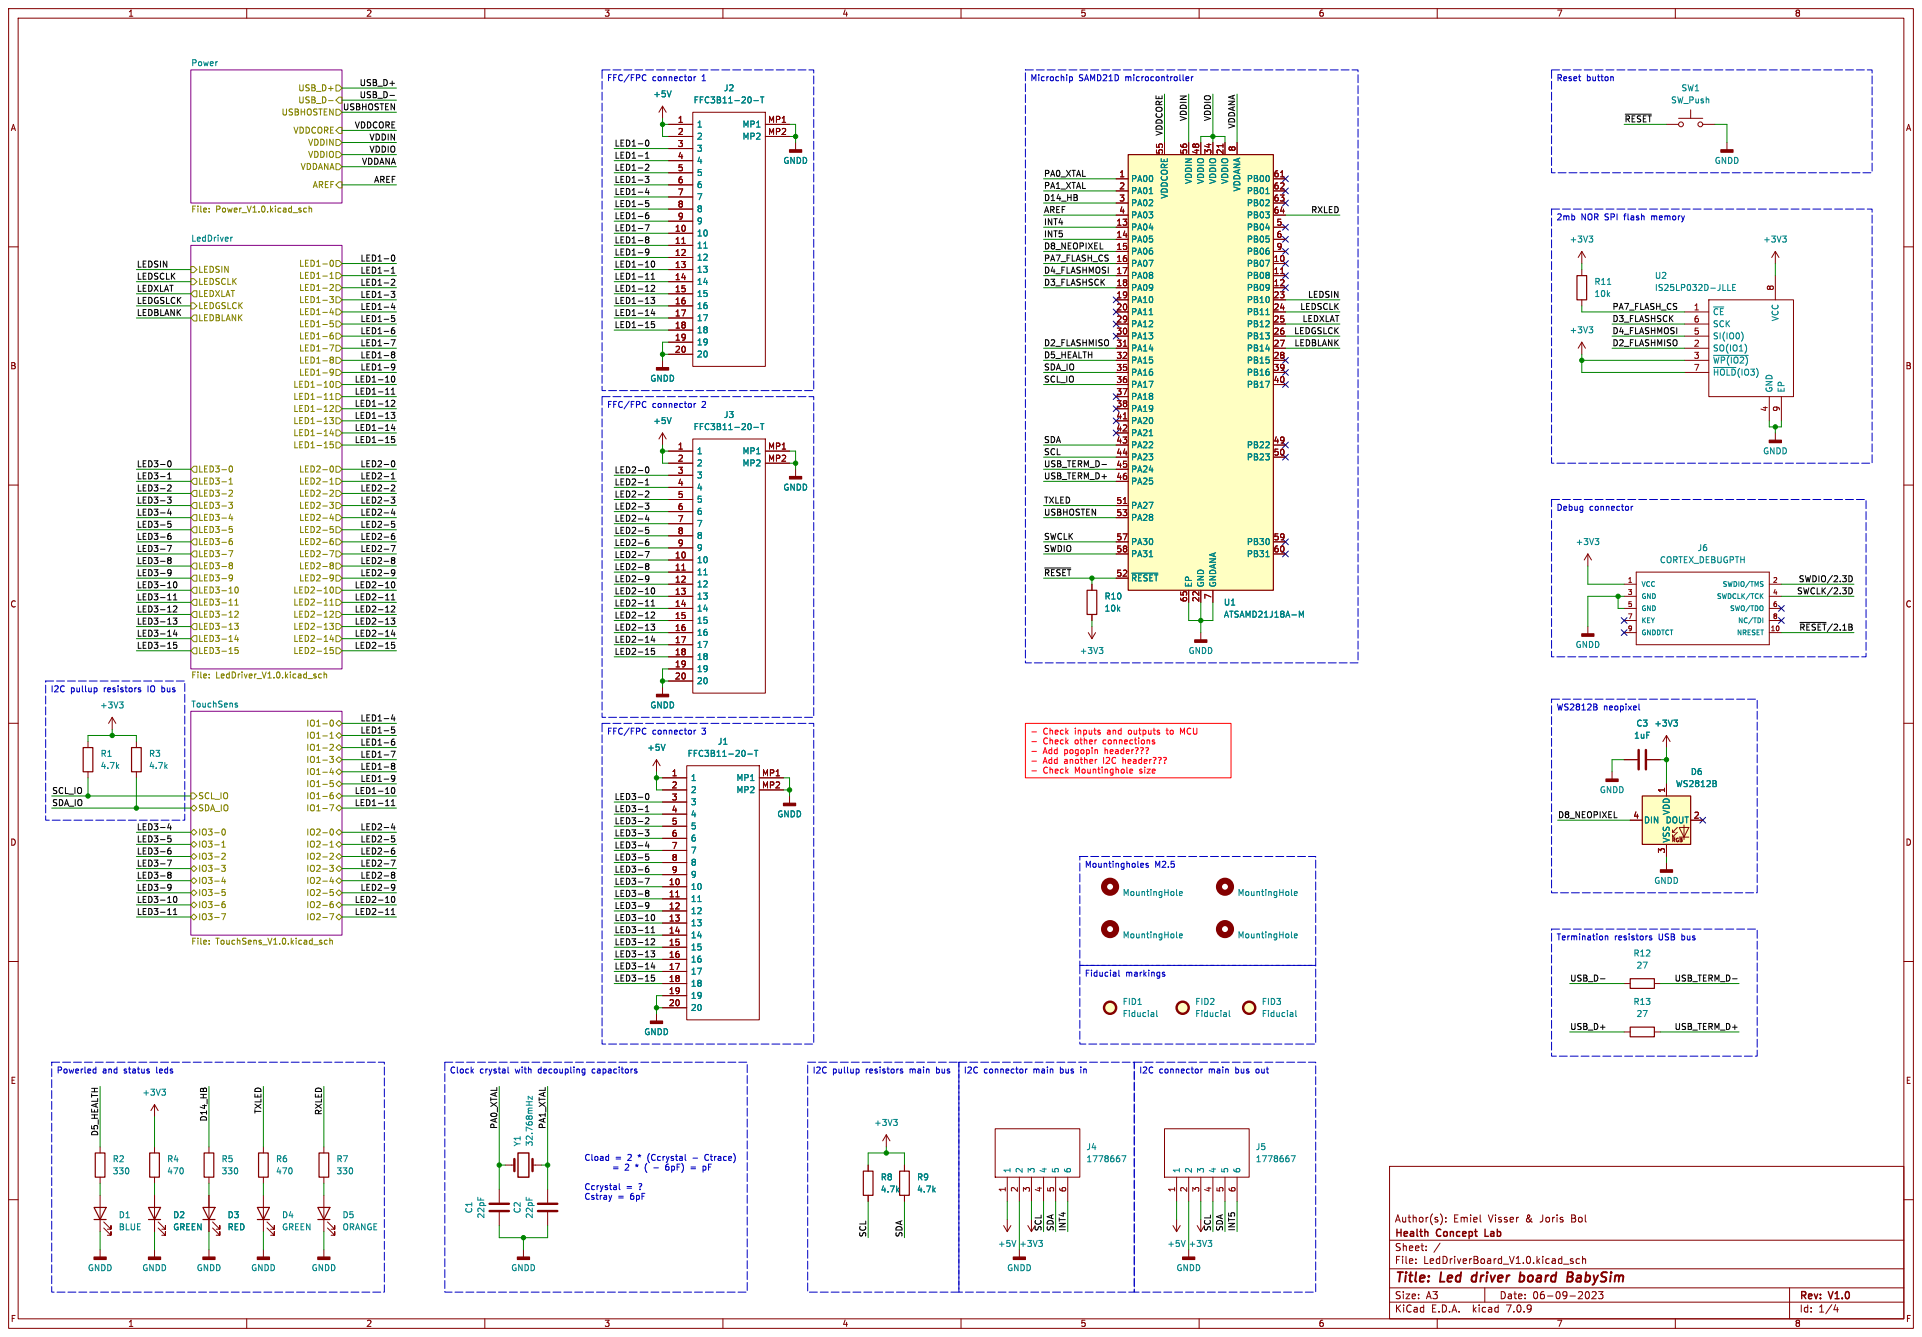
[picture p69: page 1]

2mb NOR SPI flash memory

9 ~{CE} 1 SO(IO1) 2 ~{WP(IO2)} 3 SI(IO0) 5 ~{HOLD}(IO3) 7 U2
IS25LP032D-JLLE

- Check inputs and outputs to MCU
- Check other connections
- Add pogopin header???
- Add another I2C header???
MountingHole +5V +3V3
1778667 MountingHole

Id: 1/4 Title: Led driver board BabySim

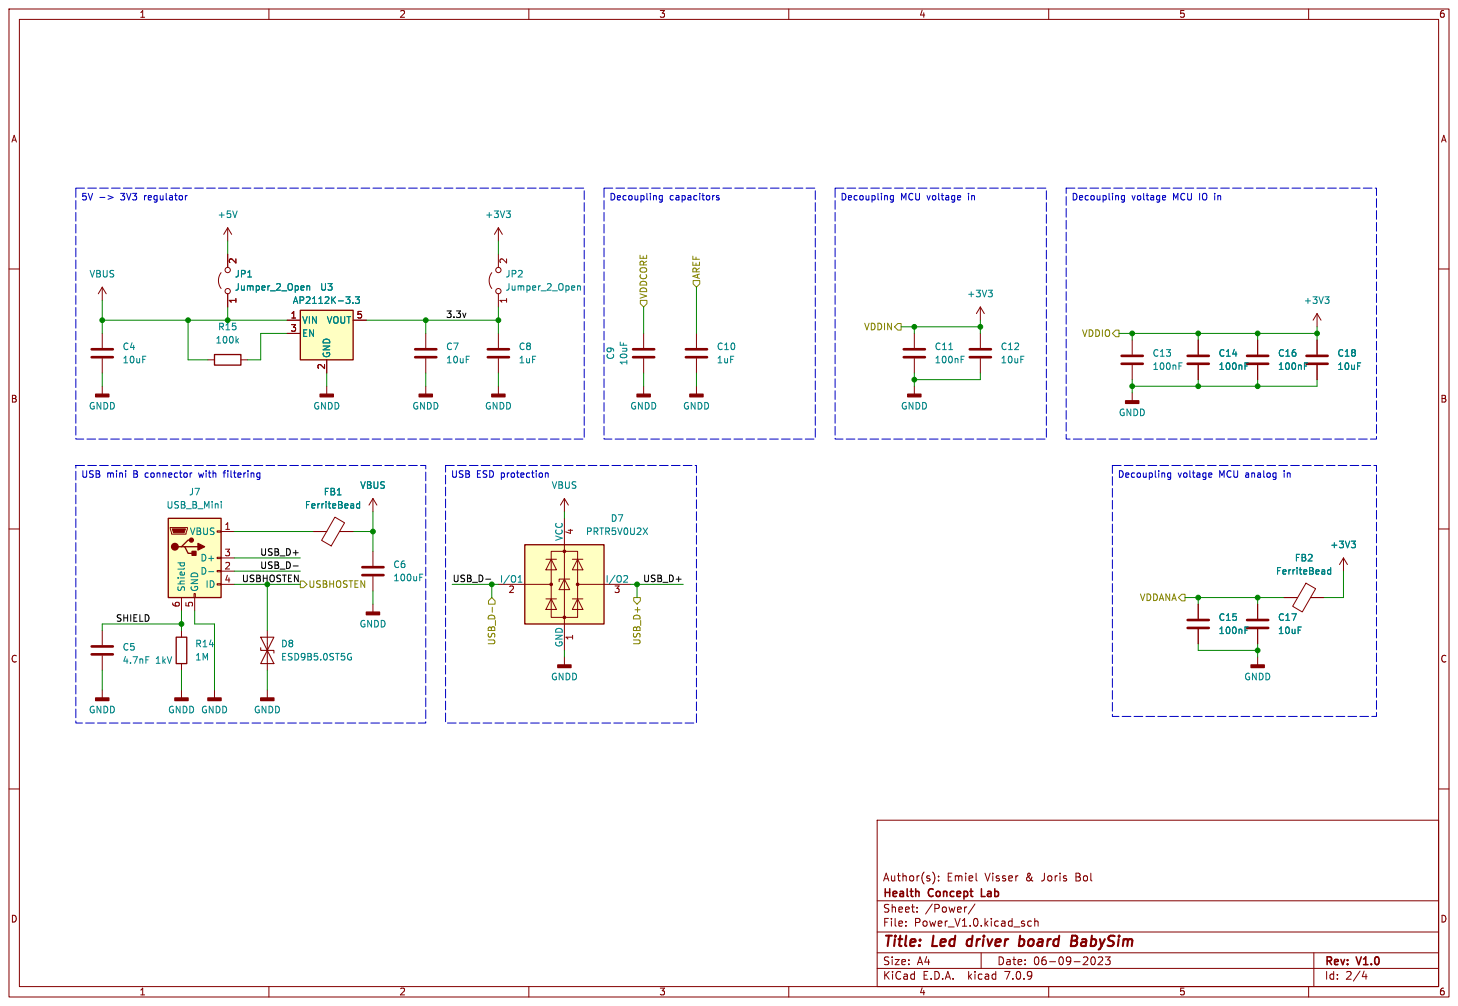
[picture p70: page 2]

Id: 2/4 Title: Led driver board BabySim

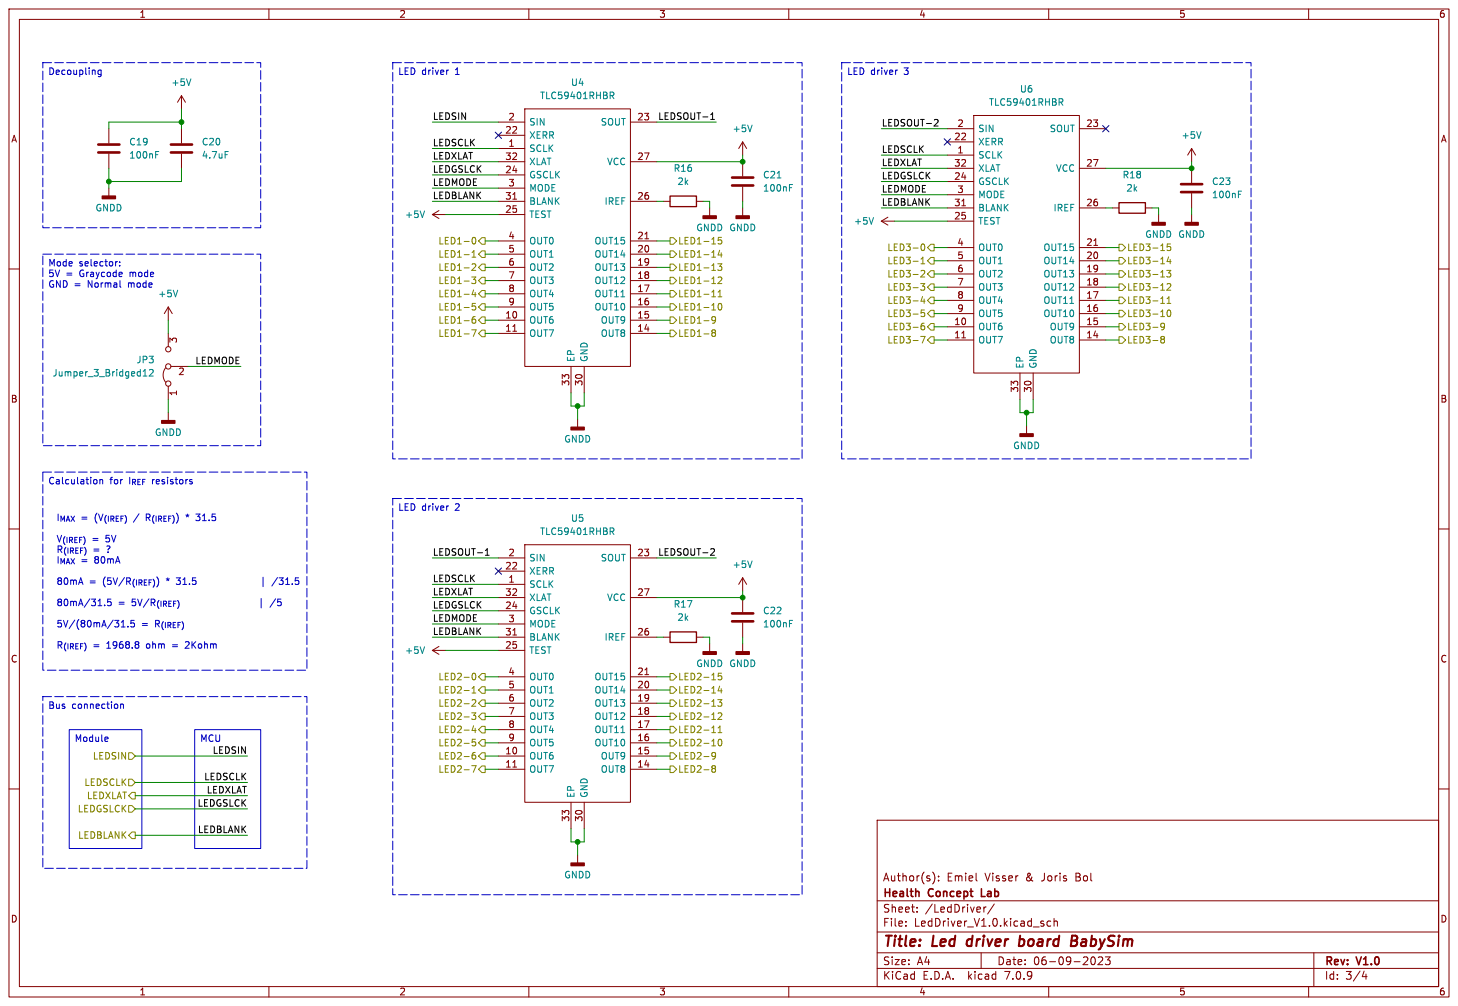
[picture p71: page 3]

I_{MAX} = (V_{(IREF)}/ R_{(IREF)})* 31.5 V_{(IREF)} = 5V R_{(IREF)} = ?

Id: 3/4 Title: Led driver board BabySim

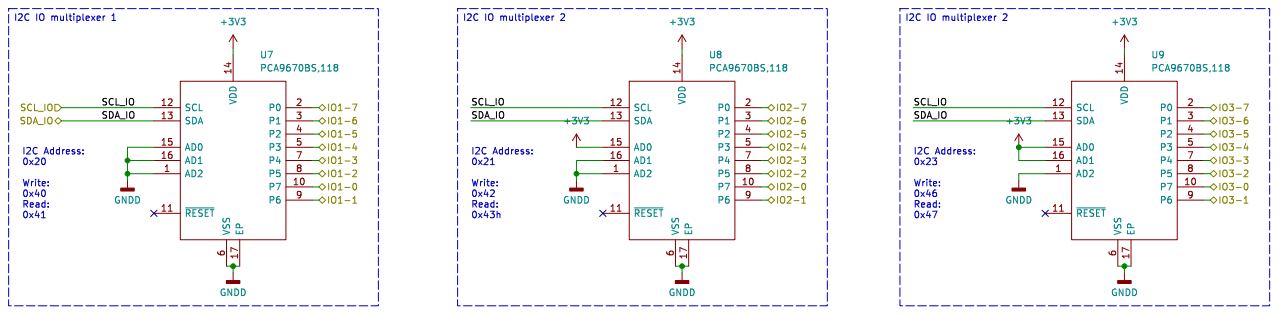
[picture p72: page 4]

Id: 4/4 Title: Led driver board BabySim

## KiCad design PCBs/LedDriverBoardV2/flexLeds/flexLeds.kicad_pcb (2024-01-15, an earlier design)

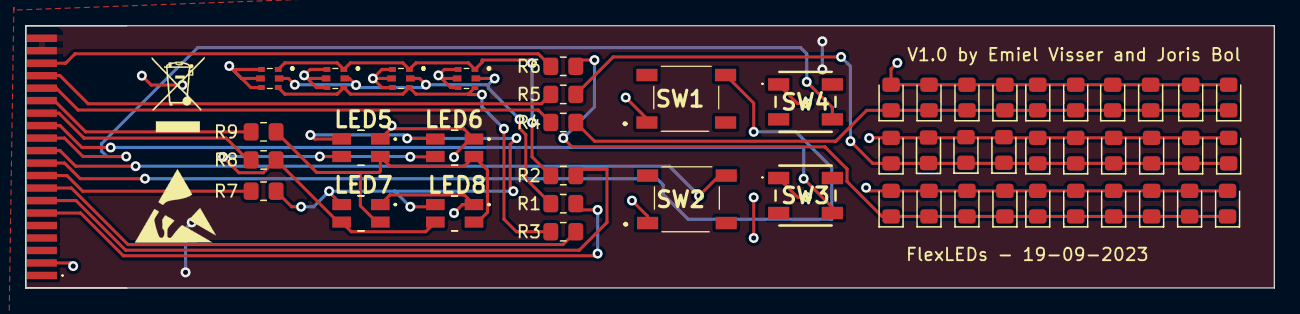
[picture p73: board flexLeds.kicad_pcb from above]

Board: 2 copper layers, 100.0 x 21.0 mm, 52 parts (0 on the bottom side), 24 nets.

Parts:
D1, D2, D3, D4, D5, D6, D7, D8, D9, D10: RED; LED_0805_2012Metric_Pad1.15x1.40mm_HandSolder
D11, D12, D13, D14, D15, D16, D17, D18, D19, D20: GREEN; LED_0805_2012Metric_Pad1.15x1.40mm_HandSolder
D21, D22, D23, D24, D25, D26, D27, D28, D29, D30: BLUE; LED_0805_2012Metric_Pad1.15x1.40mm_HandSolder
J1: Conn_01x20_Pin; Conn_1x20_FFC
LED1, LED2, LED3, LED4: 19-337C_RSBHGHC-A01_2T; 19337CRSBHGHCA012T
LED5, LED6, LED7, LED8: 150141M173100
R1, R2, R3, R4, R5, R6, R7, R8, R9: R; R_0805_2012Metric_Pad1.20x1.40mm_HandSolder
SW1, SW2: SW_Push_Dual; TL3342F260QG
SW3, SW4: SW_Push_Dual; TS174805YE160SMTTR

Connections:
+3V3: D1.2 (A), D2.2 (A), D3.2 (A), D4.2 (A), D5.2 (A), D6.2 (A), D7.2 (A), D8.2 (A), D9.2 (A), D10.2 (A), D11.2 (A), D12.2 (A), D13.2 (A), D14.2 (A), D15.2 (A), D16.2 (A), D17.2 (A), D18.2 (A), D19.2 (A), D20.2 (A), D21.2 (A), D22.2 (A), D23.2 (A), D24.2 (A), D25.2 (A), D26.2 (A), D27.2 (A), D28.2 (A), D29.2 (A), D30.2 (A), J1.2, LED1.2 (A_GREEN), LED1.4 (A_RED), LED1.6 (A_BLUE), LED2.2 (A_GREEN), LED2.4 (A_RED), LED2.6 (A_BLUE), LED3.2 (A_GREEN), LED3.4 (A_RED), LED3.6 (A_BLUE), LED4.2 (A_GREEN), LED4.4 (A_RED), LED4.6 (A_BLUE), LED5.1 (COM_A), LED6.1 (COM_A), LED7.1 (COM_A), LED8.1 (COM_A), SW1.1, SW2.1, SW3.1, SW4.1
/LED-3: J1.6, R1.1
/LED-4: J1.7, R2.1
/LED-5: J1.8, R3.1
/LED-6: J1.9, R7.1
/LED-7: J1.10, SW1.4
/LED-8: J1.11, SW2.4
/LED-9: J1.12, SW4.4
/LED-10: J1.13, SW3.4
/LED-11: J1.14, R8.1
/LED-12: J1.15, R9.1
/LED-13: J1.16, R4.2
/LED-14: J1.17, R5.2
/LED-15: J1.18, R6.2
GNDD: J1.19, J1.20
unnamed: D1.1 (K), D2.1 (K), D3.1 (K), D4.1 (K), D5.1 (K), D6.1 (K), D7.1 (K), D8.1 (K), D9.1 (K), D10.1 (K), R4.1
unnamed: D11.1 (K), D12.1 (K), D13.1 (K), D14.1 (K), D15.1 (K), D16.1 (K), D17.1 (K), D18.1 (K), D19.1 (K), D20.1 (K), R5.1
unnamed: D21.1 (K), D22.1 (K), D23.1 (K), D24.1 (K), D25.1 (K), D26.1 (K), D27.1 (K), D28.1 (K), D29.1 (K), D30.1 (K), R6.1
unnamed: LED1.5 (K_BLUE), LED2.5 (K_BLUE), LED3.5 (K_BLUE), LED4.5 (K_BLUE), R3.2
unnamed: LED1.1 (K_GREEN), LED2.1 (K_GREEN), LED3.1 (K_GREEN), LED4.1 (K_GREEN), R2.2
unnamed: LED1.3 (K_RED), LED2.3 (K_RED), LED3.3 (K_RED), LED4.3 (K_RED), R1.2
unnamed: LED5.2 (K_B), LED6.2 (K_B), LED7.2 (K_B), LED8.2 (K_B), R9.2
unnamed: LED5.4 (K_G), LED6.4 (K_G), LED7.4 (K_G), LED8.4 (K_G), R8.2
unnamed: LED5.3 (K_R), LED6.3 (K_R), LED7.3 (K_R), LED8.3 (K_R), R7.2

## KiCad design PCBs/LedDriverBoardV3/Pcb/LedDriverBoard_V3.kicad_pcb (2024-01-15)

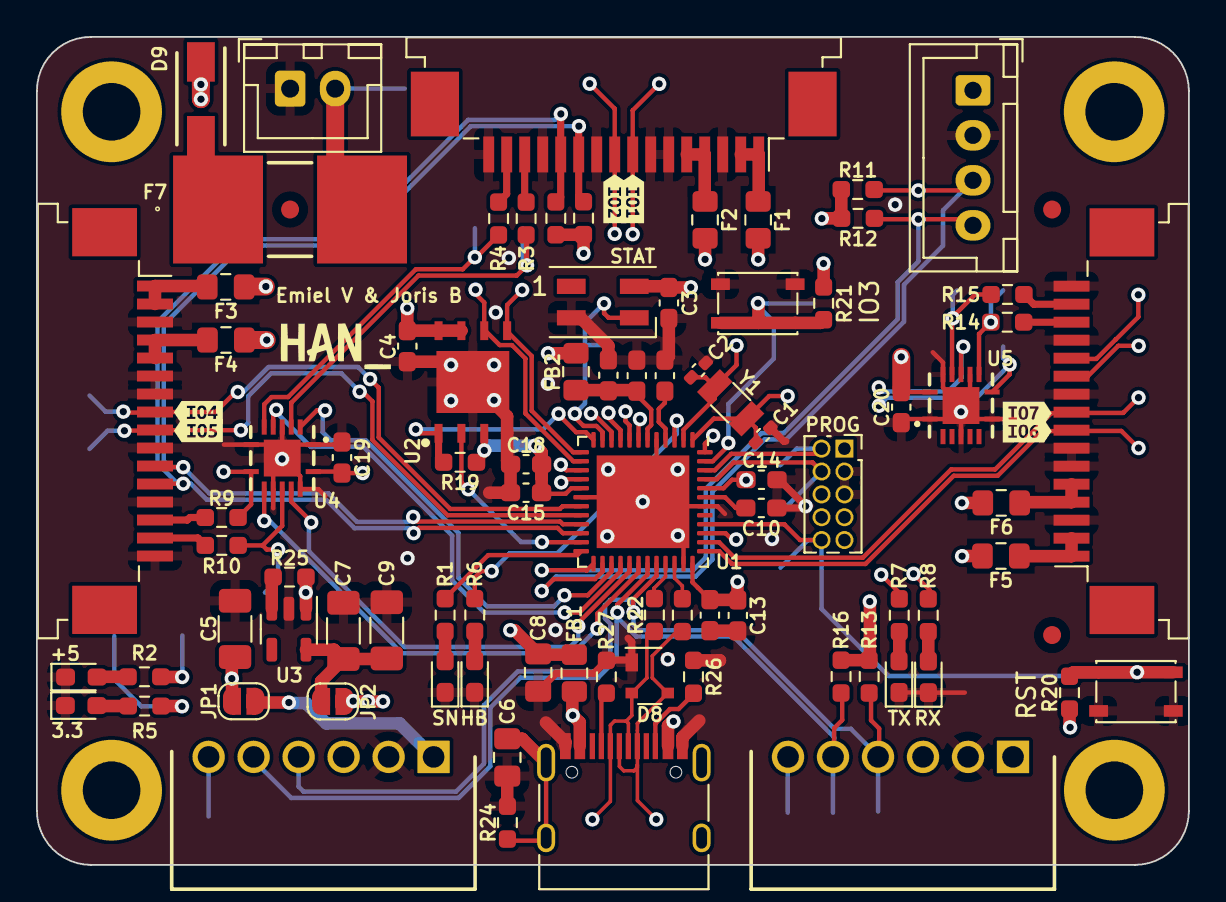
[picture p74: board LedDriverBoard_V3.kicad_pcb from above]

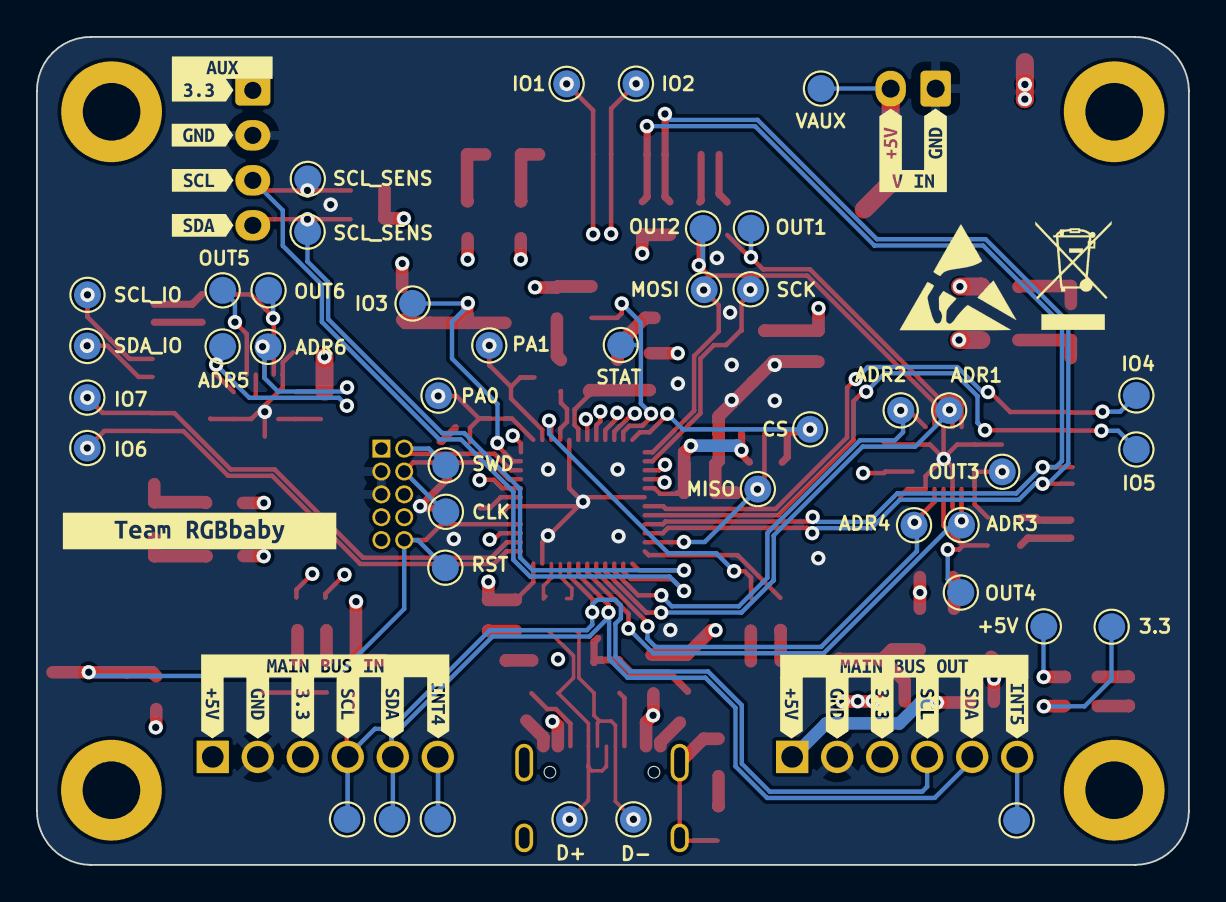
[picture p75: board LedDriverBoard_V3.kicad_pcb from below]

Board: 4 copper layers, 64.0 x 46.0 mm, 162 parts (65 on the bottom side), 78 nets.

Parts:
C1, C2: 15pF; C_0402_1005Metric_Pad0.74x0.62mm_HandSolder
C3, C11: 1uF; C_0603_1608Metric_Pad1.08x0.95mm_HandSolder
C4, C12, C14, C15, C16, C19, C20: 100nF; C_0603_1608Metric_Pad1.08x0.95mm_HandSolder
C5, C7: 10uF; C_1206_3216Metric_Pad1.33x1.80mm_HandSolder
C6: 4.7nF 1kV; C_0805_2012Metric_Pad1.18x1.45mm_HandSolder
C8: 100uF; C_0805_2012Metric_Pad1.18x1.45mm_HandSolder
C9: 1uF; C_1206_3216Metric_Pad1.33x1.80mm_HandSolder
C10, C13, C17, C18: 10uF; C_0603_1608Metric_Pad1.08x0.95mm_HandSolder
D1: BLUE; LED_0603_1608Metric_Pad1.05x0.95mm_HandSolder
D2, D4: RED; LED_0603_1608Metric_Pad1.05x0.95mm_HandSolder
D3, D5: GREEN; LED_0603_1608Metric_Pad1.05x0.95mm_HandSolder
D6: ORANGE; LED_0603_1608Metric_Pad1.05x0.95mm_HandSolder
D8: PRTR5V0U2X; SOT-143
D9: D_Schottky; DIOM5127X229N
D10: SK6812MINI; LED_SK6812MINI_PLCC4_3.5x3.5mm_P1.75mm
F1, F2, F3, F4, F5, F6: Polyfuse; Fuse_0805_2012Metric_Pad1.15x1.40mm_HandSolder
F7: Fuse; 0031.7701.11
FB1, FB2: FerriteBead; L_0805_2012Metric_Pad1.15x1.40mm_HandSolder
FID1, FID2, FID3: Fiducial; Fiducial_1mm_Mask2mm
H1, H2, H3, H4: MountingHole; MountingHole_3.2mm_M3_DIN965_Pad
J1, J2, J3: Conn_01x16_Pin; TE_1-84952-6_1x16-1MP_P1.0mm_Horizontal
J4: Conn_01x04_Socket; JST_XH_B4B-XH-A_1x04_P2.50mm_Vertical
J5, J6: 1778667; SHDRRA6W70P0X250_1X6_1670X750X510P
J7: Conn_02x05_Odd_Even; PinSocket_2x05_P1.27mm_Vertical
J8: USB_C_Receptacle_USB2.0; USB_C_Receptacle_HRO_TYPE-C-31-M-12
J9: Conn_01x02_Socket; JST_XH_B2B-XH-A_1x02_P2.50mm_Vertical
JP1, JP2: Jumper_2_Open; SolderJumper-2_P1.3mm_Open_RoundedPad1.0x1.5mm
R1, R6, R8: 330; R_0603_1608Metric_Pad0.98x0.95mm_HandSolder
R2: 2.2k; R_0603_1608Metric_Pad0.98x0.95mm_HandSolder
R3, R4, R9, R10, R14, R15: 62; R_0603_1608Metric_Pad0.98x0.95mm_HandSolder
R5, R7: 470; R_0603_1608Metric_Pad0.98x0.95mm_HandSolder
R11, R12, R13, R16, R17, R18: 4.7k; R_0603_1608Metric_Pad0.98x0.95mm_HandSolder
R19, R20, R21: 10k; R_0603_1608Metric_Pad0.98x0.95mm_HandSolder
R22, R23: 27; R_0603_1608Metric_Pad0.98x0.95mm_HandSolder
R24: 1m; R_0603_1608Metric_Pad0.98x0.95mm_HandSolder
R25: 100k; R_0603_1608Metric_Pad0.98x0.95mm_HandSolder
R26, R27: 5.1k 1%; R_0603_1608Metric_Pad0.98x0.95mm_HandSolder
SW1, SW2: SW_Push; SW_SPST_PTS810
TP1: IO_1; TestPoint_Pad_D1.5mm
TP2: IO_2; TestPoint_Pad_D1.5mm
TP3: IO_3; TestPoint_Pad_D1.5mm
TP4: IO_4; TestPoint_Pad_D1.5mm
TP5: IO_5; TestPoint_Pad_D1.5mm
TP6: IO_6; TestPoint_Pad_D1.5mm
TP7: IO_7; TestPoint_Pad_D1.5mm
TP8: CLK_A1; TestPoint_Pad_D1.5mm
TP9: CLK_A0; TestPoint_Pad_D1.5mm
TP10: INT4; TestPoint_Pad_D1.5mm
TP11: INT5; TestPoint_Pad_D1.5mm
TP12: NEOPIXEL; TestPoint_Pad_D1.5mm
TP13: SWD; TestPoint_Pad_D1.5mm
TP14: CLK; TestPoint_Pad_D1.5mm
TP15: SCL_SEN; TestPoint_Pad_D1.5mm
TP16: SDA_SEN; TestPoint_Pad_D1.5mm
TP17: RST; TestPoint_Pad_D1.5mm
TP18: CS; TestPoint_Pad_D1.5mm
TP19: SCK; TestPoint_Pad_D1.5mm
TP20: MOSI; TestPoint_Pad_D1.5mm
TP21: MISO; TestPoint_Pad_D1.5mm
TP22: SCL; TestPoint_Pad_D1.5mm
TP23: SDA; TestPoint_Pad_D1.5mm
TP24: SCL_IO; TestPoint_Pad_D1.5mm
TP25: SDA_IO; TestPoint_Pad_D1.5mm
TP26: 5V; TestPoint_Pad_D1.5mm
TP27: 3.3V; TestPoint_Pad_D1.5mm
TP28: D-; TestPoint_Pad_D1.5mm
TP29: D+; TestPoint_Pad_D1.5mm
TP30: 5V_AUX; TestPoint_Pad_D1.5mm
TP31: ADR_LED1; TestPoint_Pad_D1.5mm
TP32: ADR_LED2; TestPoint_Pad_D1.5mm
TP33: ADR_LED3; TestPoint_Pad_D1.5mm
TP34: ADR_LED4; TestPoint_Pad_D1.5mm
TP35: ADR_LED5; TestPoint_Pad_D1.5mm
TP36: ADR_LED6; TestPoint_Pad_D1.5mm
TP37: OUT_LED1; TestPoint_Pad_D1.5mm
TP38: OUT_LED2; TestPoint_Pad_D1.5mm
TP39: OUT_LED3; TestPoint_Pad_D1.5mm
TP40: OUT_LED4; TestPoint_Pad_D1.5mm
TP41: OUT_LED5; TestPoint_Pad_D1.5mm
TP42: OUT_LED6; TestPoint_Pad_D1.5mm
U1: ATSAMD21G18A-M; QFN-48-1EP_7x7mm_P0.5mm_EP5.15x5.15mm
U2: IS25LP032D-JLLE; SON127P600X500X75-9N-D
U3: AP2112K-3.3; SOT-23-5
U4, U5: SN74AHCT125RGYR; RGY-_S-PVQFN-N14_
Y1: 32.768mHz; Crystal_SMD_3215-2Pin_3.2x1.5mm
kibuzzard-6574D62C: G***; kibuzzard-6574D62C
kibuzzard-6574D547: G***; kibuzzard-6574D547
kibuzzard-6574D579: G***; kibuzzard-6574D579
kibuzzard-6574D710: G***; kibuzzard-6574D710
kibuzzard-6574D849: G***; kibuzzard-6574D849
kibuzzard-6574DAA4: G***; kibuzzard-6574DAA4
kibuzzard-6574DAAD: G***; kibuzzard-6574DAAD
kibuzzard-65744A4B, kibuzzard-65744A4B#2: G***; kibuzzard-65744A4B
kibuzzard-65744A5E, kibuzzard-65744A5E#2: G***; kibuzzard-65744A5E
kibuzzard-65744A66, kibuzzard-65744A66#2: G***; kibuzzard-65744A66
kibuzzard-65744A78, kibuzzard-65744A78#2: G***; kibuzzard-65744A78
kibuzzard-65744A88, kibuzzard-65744A88#2: G***; kibuzzard-65744A88
kibuzzard-65744B8B: G***; kibuzzard-65744B8B
kibuzzard-65744BA2: G***; kibuzzard-65744BA2
kibuzzard-65744BAF: G***; kibuzzard-65744BAF
kibuzzard-65744BC6: G***; kibuzzard-65744BC6
kibuzzard-65744BCE: G***; kibuzzard-65744BCE
kibuzzard-65744F4B: G***; kibuzzard-65744F4B
kibuzzard-65744F40: G***; kibuzzard-65744F40
kibuzzard-65744FA3: G***; kibuzzard-65744FA3
kibuzzard-65744FAF: G***; kibuzzard-65744FAF
kibuzzard-657449AF: G***; kibuzzard-657449AF
kibuzzard-6574499F: G***; kibuzzard-6574499F
kibuzzard-6574640D: G***; kibuzzard-6574640D

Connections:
+3V3: C3.2, C4.2, C12.1, C13.1, C14.1, C15.1, C18.1, D10.4 (VDD), F2.2, F4.2, F6.2, FB2.1, J4.1, J5.3, J6.3, J7.1, JP2.2 (B), R5.1, R11.1, R12.2, R13.1, R16.2, R17.1, R18.2, R19.1, R20.2, R21.2, TP27.1, U1.17 (VDDIO), U1.36 (VDDIO), U1.44 (VDDIN), U2.3 (~WP(IO2)), U2.7 (~HOLD(IO3)), U2.8 (VCC)
+5V: C19.1, C20.1, D9.1 (K), F1.2, F3.2, F5.2, J5.1, J6.1, JP1.2 (B), R2.1, TP26.1, U4.14 (VCC), U5.14 (VCC)
/ADR_LED1: TP31.1, U1.28 (PA19), U4.5 (2A)
/ADR_LED2: TP32.1, U1.27 (PA18), U4.2 (1A)
/ADR_LED3: TP33.1, U1.30 (PA21), U4.9 (3A)
/ADR_LED4: TP34.1, U1.29 (PA20), U4.12 (4A)
/ADR_LED5: TP35.1, U1.7 (PB08), U5.8 (3Y)
/ADR_LED6: TP36.1, U1.8 (PB09), U5.11 (4Y)
/AREF: C11.1, U1.4 (PA03)
/D2_FLASHMISO: TP21.1, U1.23 (PA14), U2.2 (SO(IO1))
/D3_FLASHSCK: TP19.1, U1.14 (PA09), U2.6 (SCK)
/D4_FLASHMOSI: TP20.1, U1.13 (PA08), U2.5 (SI(IO0))
/D5_HEALTH: R1.1, U1.24 (PA15)
/D8_NEOPIXEL: D10.3 (DIN), TP12.1, U1.11 (PA06)
/D14_HB: R6.1, U1.3 (PA02)
/INT4: J5.6, TP10.1, U1.9 (PA04)
/INT5: J6.6, TP11.1, U1.10 (PA05)
/IO_1: J1.8, TP1.1, U1.15 (PA10)
/IO_2: J1.9, TP2.1, U1.16 (PA11)
/IO_3: R21.1, SW2.1, TP3.1, U1.47 (PB02)
/IO_4: J2.8, TP4.1, U1.19 (PB10)
/IO_5: J2.9, TP5.1, U1.20 (PB11)
/IO_6: J3.8, TP6.1, U1.37 (PB22)
/IO_7: J3.9, TP7.1, U1.38 (PB23)
/OUT_LED1: R4.1, TP37.1, U4.6 (2Y)
/OUT_LED2: R3.1, TP38.1, U4.3 (1Y)
/OUT_LED3: R9.1, TP39.1, U4.8 (3Y)
/OUT_LED4: R10.1, TP40.1, U4.11 (4Y)
/OUT_LED5: R14.1, TP41.1, U5.9 (3A)
/OUT_LED6: R15.1, TP42.1, U5.12 (4A)
/PA0_XTAL: C1.2, TP9.1, U1.1 (PA00), Y1.2
/PA1_XTAL: C2.2, TP8.1, U1.2 (PA01), Y1.1
/PA7_FLASH_CS: R19.2, TP18.1, U1.12 (PA07), U2.1 (~CE)
/Power/3.3v: C7.1, C9.1, JP2.1 (A), U3.5 (VOUT)
/Power/SHIELD: C6.1, J8.S1 (SHIELD), R24.1
/RXLED: R8.1, U1.48 (PB03)
/SCL: J5.4, J6.4, R13.2, TP22.1, U1.32 (PA23)
/SCL_IO: J1.12, J2.12, J3.12, R17.2, TP24.1, U1.22 (PA13)
/SCL_SENSOR_D13: J4.3, R11.2, TP15.1, U1.26 (PA17)
/SDA: J5.5, J6.5, R16.1, TP23.1, U1.31 (PA22)
/SDA_IO: J1.11, J2.11, J3.11, R18.1, TP25.1, U1.21 (PA12)
/SDA_SENSOR_D11: J4.4, R12.1, TP16.1, U1.25 (PA16)
/SWCLK: J7.4, TP14.1, U1.45 (PA30)
/SWDIO: J7.2, TP13.1, U1.46 (PA31)
/TXLED: R7.1, U1.39 (PA27)
/USB_D+: D8.3 (I/O2), J8.A6 (D+), J8.B6 (D+), R23.1, TP29.1
/USB_D-: D8.2 (I/O1), J8.A7 (D-), J8.B7 (D-), R22.1, TP28.1
/USB_TERM_D+: R23.2, U1.34 (PA25)
/USB_TERM_D-: R22.2, U1.33 (PA24)
/VDDANA: C16.1, C17.1, FB2.2, U1.6 (VDDANA)
/VDDCORE: C10.2, U1.43 (VDDCORE)
/~RESET: J7.10, R20.1, SW1.1, TP17.1, U1.40 (~RESET)
GNDD: C1.1, C2.1, C3.1, C4.1, C5.2, C6.2, C7.2, C8.2, C9.2, C10.1, C11.2, C12.2, C13.2, C14.2, C15.2, C16.2, C17.2, C18.2, C19.2, C20.2, D1.1 (K), D2.1 (K), D3.1 (K), D4.1 (K), D5.1 (K), D6.1 (K), D8.1 (GND), D10.2 (VSS), J1.3, J1.6, J1.7, J1.10, J1.13, J1.16, J2.3, J2.6, J2.7, J2.10, J2.13, J2.16, J3.3, J3.6, J3.7, J3.10, J3.13, J3.16, J4.2, J5.2, J6.2, J7.3, J7.5, J8.A1 (GND), J8.A12 (GND), J8.B1 (GND), J8.B12 (GND), J9.1, R24.2, R26.2, R27.2, SW1.2, SW2.2, U1.5 (GNDANA), U1.18 (GND), U1.35 (GND), U1.42 (GND), U1.49 (EP), U2.4 (GND), U2.9 (EP), U3.2 (GND), U4.1 (1~OE), U4.4 (2~OE), U4.7 (GND), U4.10 (3~OE), U4.13 (4~OE), U4.15 (THERMAL_PAD), U5.1 (1~OE), U5.4 (2~OE), U5.7 (GND), U5.10 (3~OE), U5.13 (4~OE), U5.15 (THERMAL_PAD)
unnamed: D1.2 (A), R1.2
unnamed: D2.2 (A), R2.2
unnamed: D3.2 (A), R5.2
unnamed: D4.2 (A), R6.2
unnamed: D5.2 (A), R7.2
unnamed: D6.2 (A), R8.2
unnamed: D9.2 (A), F7.1
unnamed: FB1.1, J8.A4 (VBUS), J8.A9 (VBUS), J8.B4 (VBUS), J8.B9 (VBUS)
unnamed: F1.1, J1.1, J1.2
unnamed: F2.1, J1.4, J1.5
unnamed: J1.14, R3.2
unnamed: J1.15, R4.2
unnamed: F3.1, J2.1, J2.2
unnamed: F4.1, J2.4, J2.5
unnamed: J2.14, R9.2
unnamed: J2.15, R10.2
unnamed: F5.1, J3.1, J3.2
unnamed: F6.1, J3.4, J3.5
unnamed: J3.14, R14.2
unnamed: J3.15, R15.2
unnamed: J8.A5 (CC1), R27.1
unnamed: J8.B5 (CC2), R26.1
unnamed: F7.2, J9.2, TP30.1
unnamed: R25.2, U3.3 (EN)
VBUS: C5.1, C8.1, D8.4 (VCC), FB1.2, JP1.1 (A), R25.1, U3.1 (VIN)

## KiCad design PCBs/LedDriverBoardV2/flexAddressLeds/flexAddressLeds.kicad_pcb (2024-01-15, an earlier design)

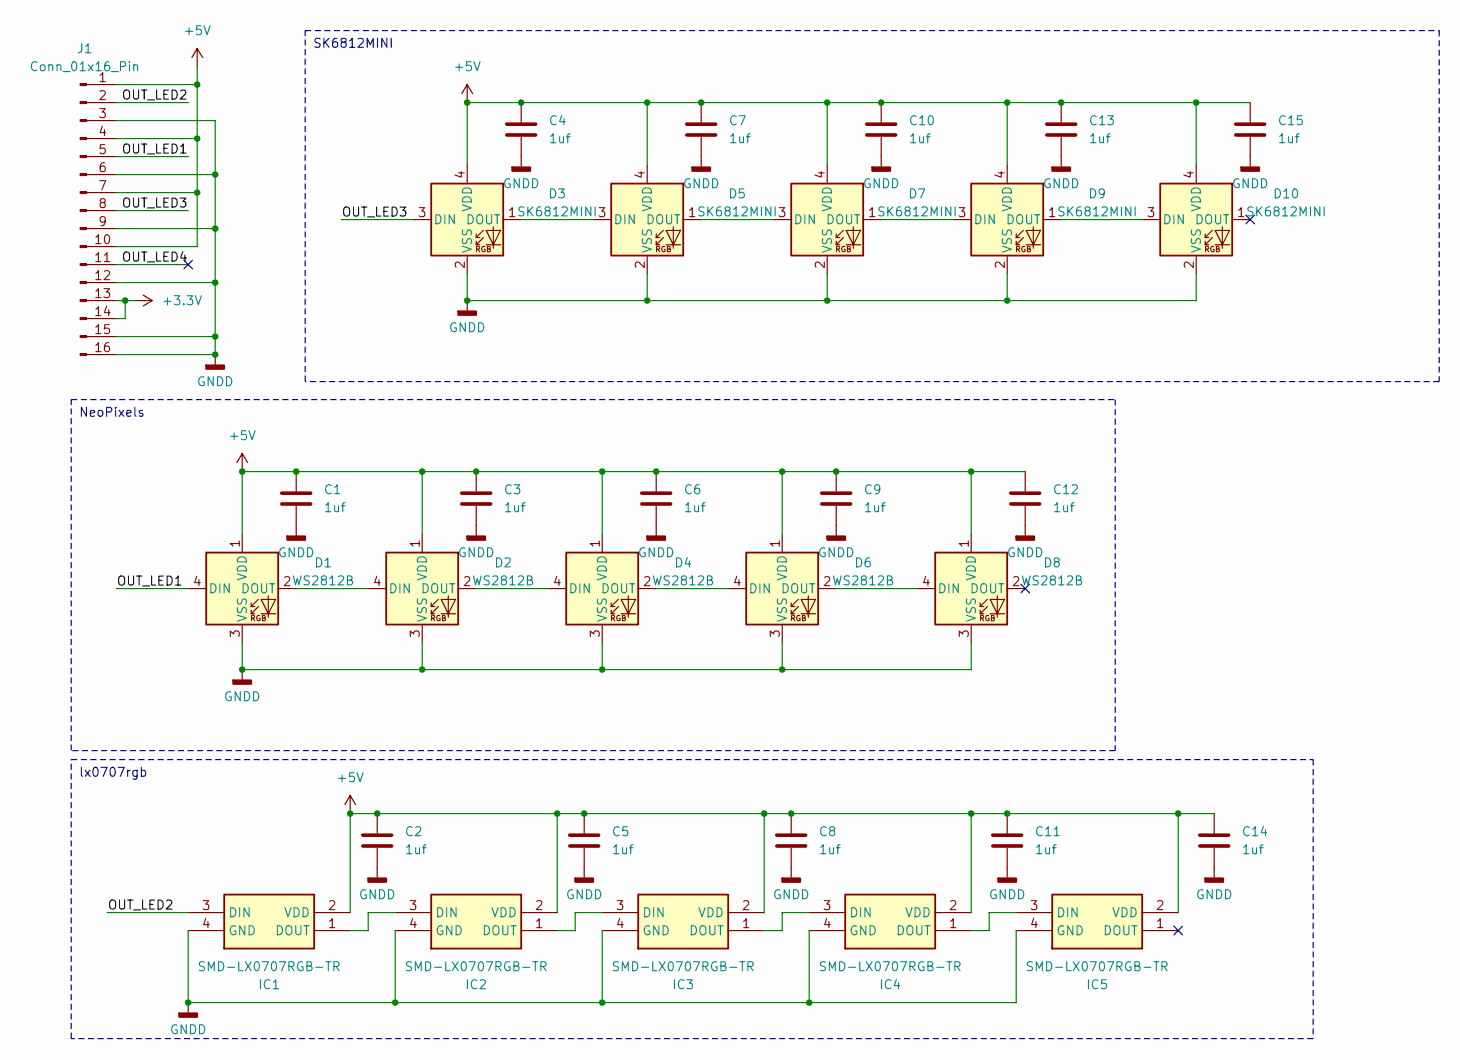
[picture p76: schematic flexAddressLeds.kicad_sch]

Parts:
C1, C2, C3, C4, C5, C6, C7, C8, C9, C10, C11, C12, C13, C14, C15: 1uf; C_0603_1608Metric_Pad1.08x0.95mm_HandSolder
D1, D2, D4, D6, D8: WS2812B; LED_WS2812B_PLCC4_5.0x5.0mm_P3.2mm
D3, D5, D7, D9, D10: SK6812MINI; LED_SK6812MINI_PLCC4_3.5x3.5mm_P1.75mm
IC1, IC2, IC3, IC4, IC5: SMD-LX0707RGB-TR; SMDLX0707RGBTR; Manufacturer_Part_Number SMD-LX0707RGB-TR; Mouser Part Number 696-SMDLX0707RGBTR
J1: Conn_01x16_Pin; Conn_1x16_FFC

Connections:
+3.3V: J1.13, J1.14
+5V: C1.1, C2.1, C3.1, C4.1, C5.1, C6.1, C7.1, C8.1, C9.1, C10.1, C11.1, C12.1, C13.1, C14.1, C15.1, D1.1 (VDD), D2.1 (VDD), D3.4 (VDD), D4.1 (VDD), D5.4 (VDD), D6.1 (VDD), D7.4 (VDD), D8.1 (VDD), D9.4 (VDD), D10.4 (VDD), IC1.2 (VDD), IC2.2 (VDD), IC3.2 (VDD), IC4.2 (VDD), IC5.2 (VDD), J1.1, J1.4, J1.7, J1.10
/OUT_LED1: D1.4 (DIN), J1.5
/OUT_LED2: IC1.3 (DIN), J1.2
/OUT_LED3: D3.3 (DIN), J1.8
/OUT_LED4: J1.11
GNDD: C1.2, C2.2, C3.2, C4.2, C5.2, C6.2, C7.2, C8.2, C9.2, C10.2, C11.2, C12.2, C13.2, C14.2, C15.2, D1.3 (VSS), D2.3 (VSS), D3.2 (VSS), D4.3 (VSS), D5.2 (VSS), D6.3 (VSS), D7.2 (VSS), D8.3 (VSS), D9.2 (VSS), D10.2 (VSS), IC1.4 (GND), IC2.4 (GND), IC3.4 (GND), IC4.4 (GND), IC5.4 (GND), J1.3, J1.6, J1.9, J1.12, J1.15, J1.16
unnamed: D1.2 (DOUT), D2.4 (DIN)
unnamed: D2.2 (DOUT), D4.4 (DIN)
unnamed: D3.1 (DOUT), D5.3 (DIN)
unnamed: D4.2 (DOUT), D6.4 (DIN)
unnamed: D5.1 (DOUT), D7.3 (DIN)
unnamed: D6.2 (DOUT), D8.4 (DIN)
unnamed: D7.1 (DOUT), D9.3 (DIN)
unnamed: D9.1 (DOUT), D10.3 (DIN)
unnamed: IC1.1 (DOUT), IC2.3 (DIN)
unnamed: IC2.1 (DOUT), IC3.3 (DIN)
unnamed: IC3.1 (DOUT), IC4.3 (DIN)
unnamed: IC4.1 (DOUT), IC5.3 (DIN)

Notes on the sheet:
lx0707rgb
NeoPixels
SK6812MINI

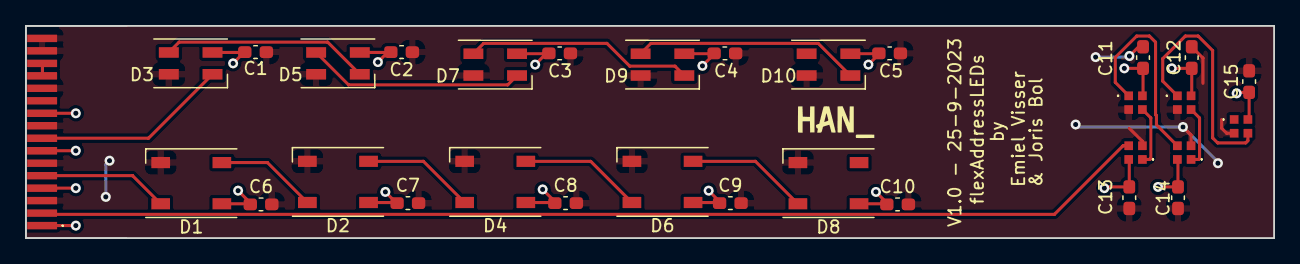
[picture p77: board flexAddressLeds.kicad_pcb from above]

Board: 2 copper layers, 100.0 x 17.0 mm, 31 parts (0 on the bottom side), 18 nets.

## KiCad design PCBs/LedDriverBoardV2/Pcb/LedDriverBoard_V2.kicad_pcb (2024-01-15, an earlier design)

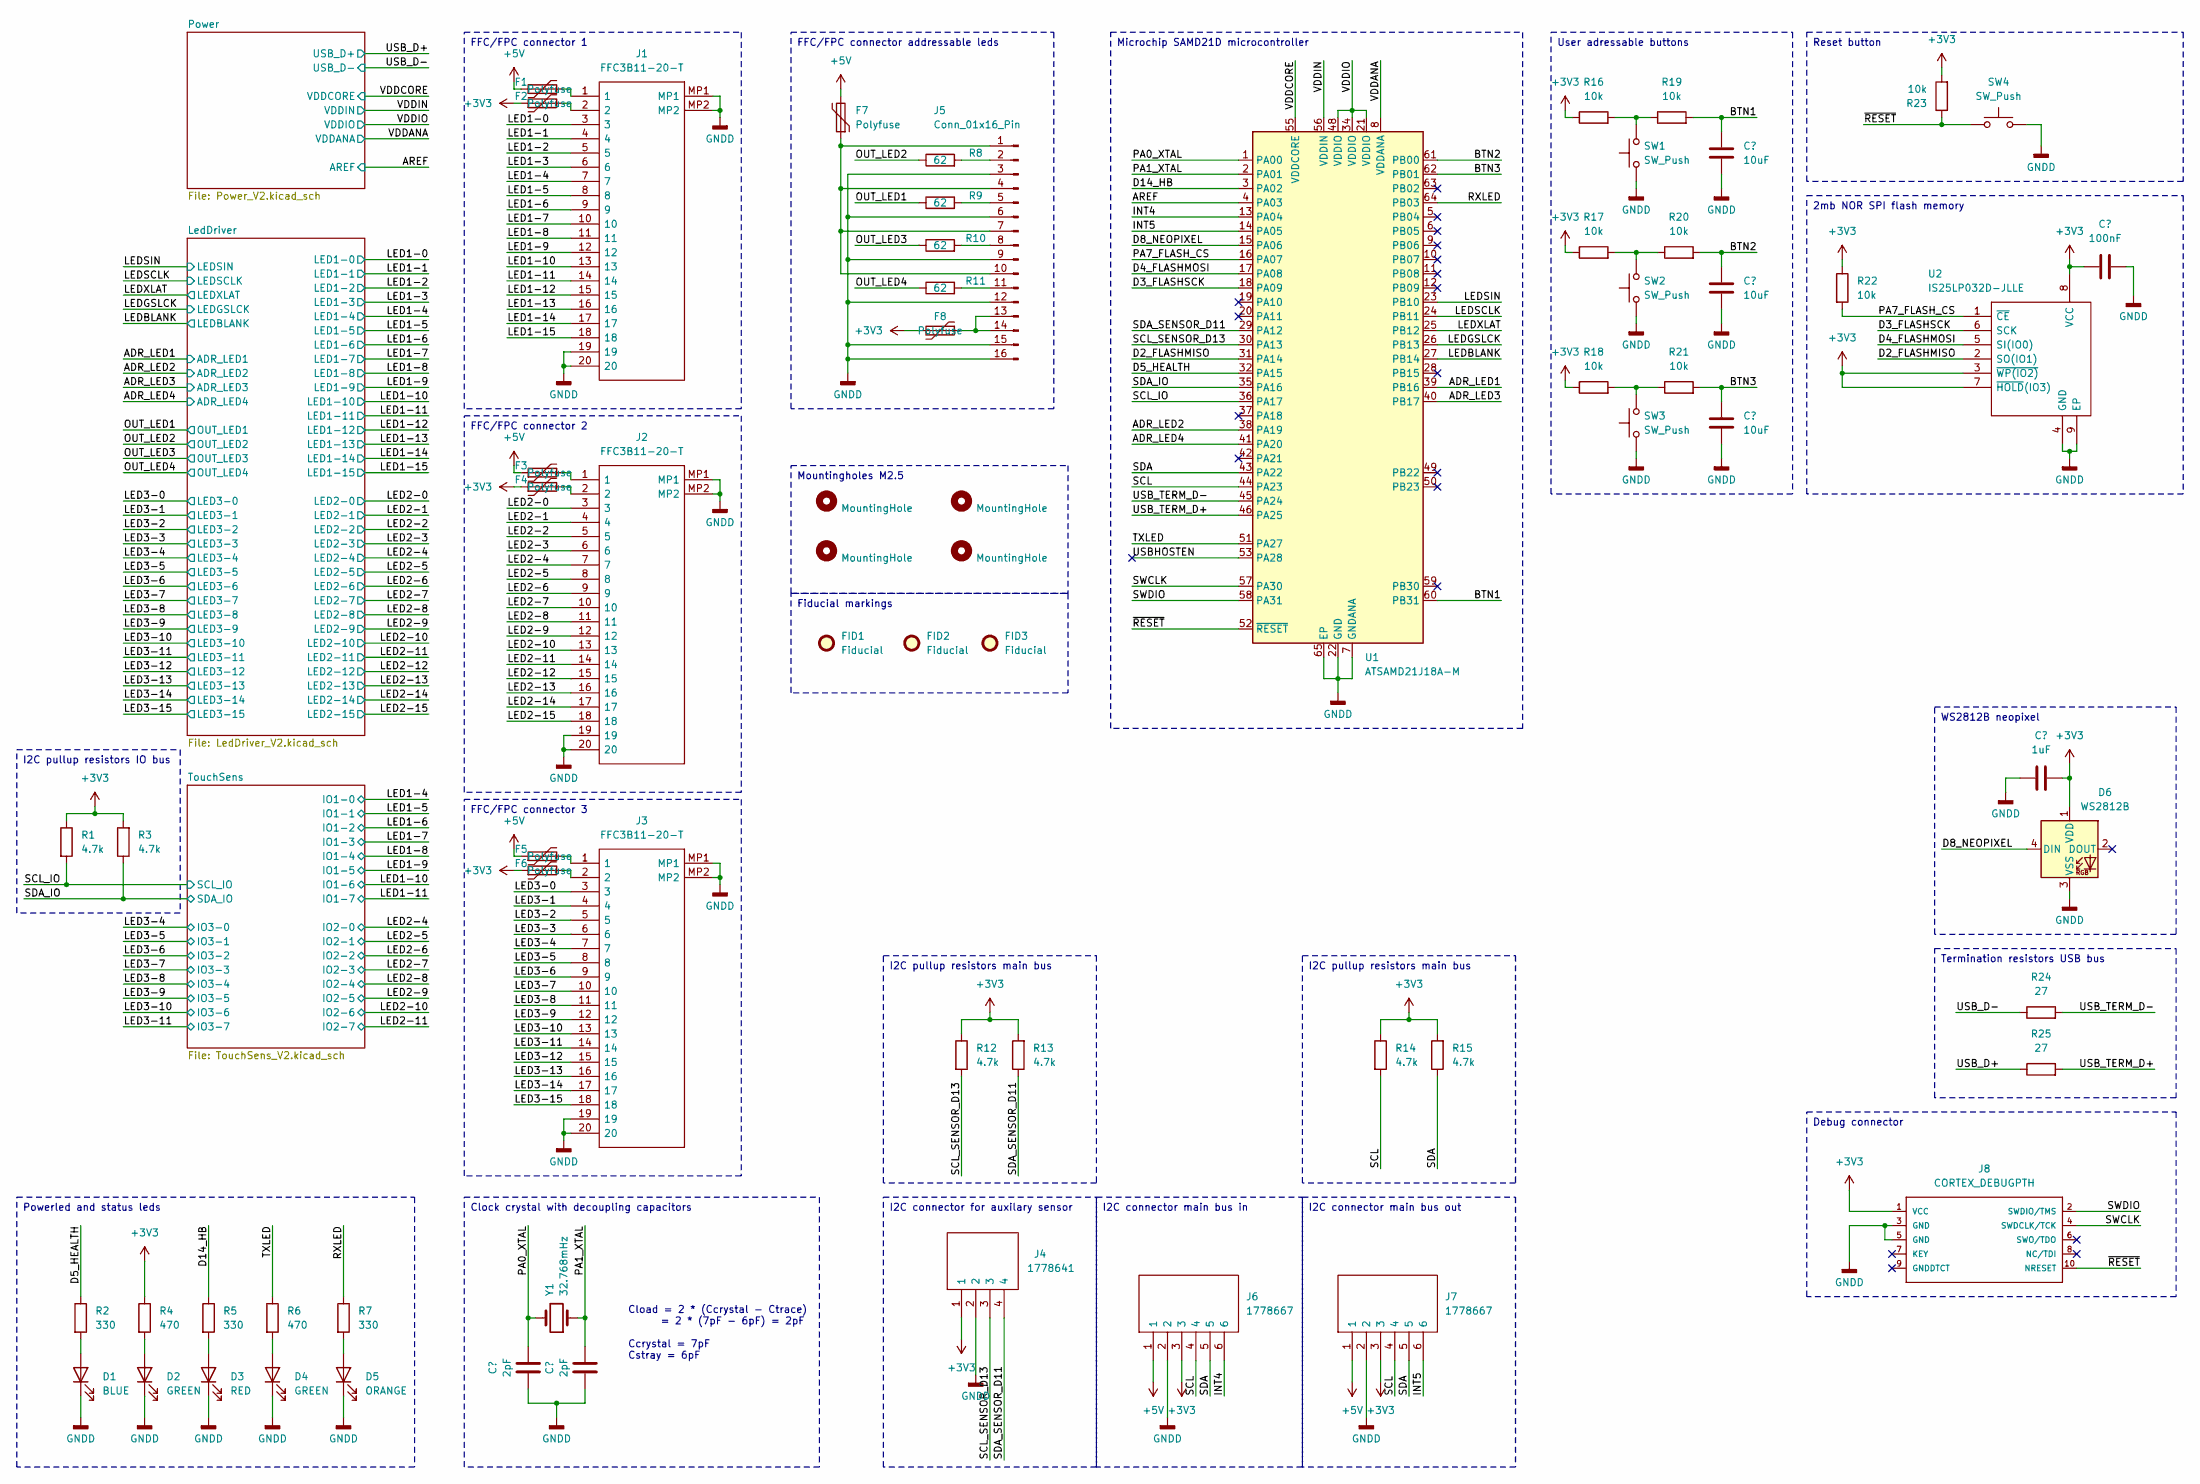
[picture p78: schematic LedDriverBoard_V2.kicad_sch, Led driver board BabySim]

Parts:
C1, C2: 2pF; C_0402_1005Metric_Pad0.74x0.62mm_HandSolder
C3, C4, C5: 10uF; C_0603_1608Metric_Pad1.08x0.95mm_HandSolder
C6: 1uF; C_0603_1608Metric_Pad1.08x0.95mm_HandSolder
C7: 100nF; C_0603_1608Metric_Pad1.08x0.95mm_HandSolder
D1: BLUE; LED_0805_2012Metric_Pad1.15x1.40mm_HandSolder
D2, D4: GREEN; LED_0805_2012Metric_Pad1.15x1.40mm_HandSolder
D3: RED; LED_0805_2012Metric_Pad1.15x1.40mm_HandSolder
D5: ORANGE; LED_0805_2012Metric_Pad1.15x1.40mm_HandSolder
D6: WS2812B; LED_WS2812B_PLCC4_5.0x5.0mm_P3.2mm
F1, F2, F3, F4, F5, F6, F7, F8: Polyfuse; Fuse_0805_2012Metric_Pad1.15x1.40mm_HandSolder
FID1, FID2, FID3: Fiducial; Fiducial_1mm_Mask2mm
H1, H2, H3, H4: MountingHole; MountingHole_3.2mm_M3_DIN965
J1, J2, J3: FFC3B11-20-T; FFC3B1120T; Manufacturer_Part_Number FFC3B11-20-T; Mouser Part Number 640-FFC3B11-20-T
J4: 1778641; SHDRRA4W60P0X250_1X4_1170X750X510P; Manufacturer_Part_Number 1778641; Mouser Part Number 651-1778641
J5: Conn_01x16_Pin; TE_1-84952-6_1x16-1MP_P1.0mm_Horizontal
J6, J7: 1778667; SHDRRA6W70P0X250_1X6_1670X750X510P; Manufacturer_Part_Number 1778667; Mouser Part Number 651-1778667
J8: CORTEX_DEBUGPTH; 2X5-PTH-1.27MM
R1, R3, R12, R13, R14, R15: 4.7k; R_0603_1608Metric_Pad0.98x0.95mm_HandSolder
R2, R5, R7: 330; R_0603_1608Metric_Pad0.98x0.95mm_HandSolder
R4, R6: 470; R_0603_1608Metric_Pad0.98x0.95mm_HandSolder
R8, R9, R10, R11: 62; R_0603_1608Metric_Pad0.98x0.95mm_HandSolder
R16, R17, R18, R19, R20, R21, R22, R23: 10k; R_0603_1608Metric_Pad0.98x0.95mm_HandSolder
R24, R25: 27; R_0603_1608Metric_Pad0.98x0.95mm_HandSolder
SW1, SW2, SW3, SW4: SW_Push; SW_SPST_B3U-1000P
U1: ATSAMD21J18A-M; QFN-64-1EP_9x9mm_P0.5mm_EP4.7x4.7mm
U2: IS25LP032D-JLLE; SON127P600X500X75-9N-D; Manufacturer_Part_Number IS25LP032D-JLLE; Mouser Part Number 870-IS25LP032D-JLLE
Y1: 32.768mHz; Crystal_SMD_3215-2Pin_3.2x1.5mm

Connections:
+5V: F1.1, F3.1, F5.1, F7.2, J6.1, J7.1; also elsewhere on the board
/ADR_LED1: U1.39 (PB16); also elsewhere on the board
/ADR_LED2: U1.38 (PA19); also elsewhere on the board
/ADR_LED3: U1.40 (PB17); also elsewhere on the board
/ADR_LED4: U1.41 (PA20); also elsewhere on the board
/AREF: U1.4 (PA03); also elsewhere on the board
/BTN1: C3.1, R19.2, U1.60 (PB31)
/BTN2: C4.1, R20.2, U1.61 (PB00)
/BTN3: C5.1, R21.2, U1.62 (PB01)
/D2_FLASHMISO: U1.31 (PA14), U2.2 (SO(IO1))
/D3_FLASHSCK: U1.18 (PA09), U2.6 (SCK)
/D4_FLASHMOSI: U1.17 (PA08), U2.5 (SI(IO0))
/D5_HEALTH: R2.1, U1.32 (PA15)
/D8_NEOPIXEL: D6.4 (DIN), U1.15 (PA06)
/D14_HB: R5.1, U1.3 (PA02)
/INT4: J6.6, U1.13 (PA04)
/INT5: J7.6, U1.14 (PA05)
/LED1-0: J1.3; also elsewhere on the board
/LED1-1: J1.4; also elsewhere on the board
/LED1-2: J1.5; also elsewhere on the board
/LED1-3: J1.6; also elsewhere on the board
/LED1-4: J1.7; also elsewhere on the board
/LED1-5: J1.8; also elsewhere on the board
/LED1-6: J1.9; also elsewhere on the board
/LED1-7: J1.10; also elsewhere on the board
/LED1-8: J1.11; also elsewhere on the board
/LED1-9: J1.12; also elsewhere on the board
/LED1-10: J1.13; also elsewhere on the board
/LED1-11: J1.14; also elsewhere on the board
/LED1-12: J1.15; also elsewhere on the board
/LED1-13: J1.16; also elsewhere on the board
/LED1-14: J1.17; also elsewhere on the board
/LED1-15: J1.18; also elsewhere on the board
/LED2-0: J2.3; also elsewhere on the board
/LED2-1: J2.4; also elsewhere on the board
/LED2-2: J2.5; also elsewhere on the board
/LED2-3: J2.6; also elsewhere on the board
/LED2-4: J2.7; also elsewhere on the board
/LED2-5: J2.8; also elsewhere on the board
/LED2-6: J2.9; also elsewhere on the board
/LED2-7: J2.10; also elsewhere on the board
/LED2-8: J2.11; also elsewhere on the board
/LED2-9: J2.12; also elsewhere on the board
/LED2-10: J2.13; also elsewhere on the board
/LED2-11: J2.14; also elsewhere on the board
/LED2-12: J2.15; also elsewhere on the board
/LED2-13: J2.16; also elsewhere on the board
/LED2-14: J2.17; also elsewhere on the board
/LED2-15: J2.18; also elsewhere on the board
/LED3-0: J3.3; also elsewhere on the board
/LED3-1: J3.4; also elsewhere on the board
/LED3-2: J3.5; also elsewhere on the board
/LED3-3: J3.6; also elsewhere on the board
/LED3-4: J3.7; also elsewhere on the board
/LED3-5: J3.8; also elsewhere on the board
/LED3-6: J3.9; also elsewhere on the board
/LED3-7: J3.10; also elsewhere on the board
/LED3-8: J3.11; also elsewhere on the board
/LED3-9: J3.12; also elsewhere on the board
/LED3-10: J3.13; also elsewhere on the board
/LED3-11: J3.14; also elsewhere on the board
/LED3-12: J3.15; also elsewhere on the board
/LED3-13: J3.16; also elsewhere on the board
/LED3-14: J3.17; also elsewhere on the board
/LED3-15: J3.18; also elsewhere on the board
/LEDBLANK: U1.27 (PB14); also elsewhere on the board
/LEDGSLCK: U1.26 (PB13); also elsewhere on the board
/LEDSCLK: U1.24 (PB11); also elsewhere on the board
/LEDSIN: U1.23 (PB10); also elsewhere on the board
/LEDXLAT: U1.25 (PB12); also elsewhere on the board
/OUT_LED1: R9.1; also elsewhere on the board
/OUT_LED2: R8.1; also elsewhere on the board
/OUT_LED3: R10.1; also elsewhere on the board
/OUT_LED4: R11.1; also elsewhere on the board
/PA0_XTAL: C1.2, U1.1 (PA00), Y1.2
/PA1_XTAL: C2.2, U1.2 (PA01), Y1.1
/PA7_FLASH_CS: R22.2, U1.16 (PA07), U2.1 (~CE)
/RXLED: R7.1, U1.64 (PB03)
/SCL: J6.4, J7.4, R14.2, U1.44 (PA23)
/SCL_IO: R1.2, U1.36 (PA17); also elsewhere on the board
/SCL_SENSOR_D13: J4.3, R12.2, U1.30 (PA13)
/SDA: J6.5, J7.5, R15.1, U1.43 (PA22)
/SDA_IO: R3.1, U1.35 (PA16); also elsewhere on the board
/SDA_SENSOR_D11: J4.4, R13.1, U1.29 (PA12)
/SWCLK: J8.4 (SWDCLK/TCK), U1.57 (PA30)
/SWDIO: J8.2 (SWDIO/TMS), U1.58 (PA31)
/TXLED: R6.1, U1.51 (PA27)
/USBHOSTEN: U1.53 (PA28)
/USB_D+: R25.1; also elsewhere on the board
/USB_D-: R24.1; also elsewhere on the board
/USB_TERM_D+: R25.2, U1.46 (PA25)
/USB_TERM_D-: R24.2, U1.45 (PA24)
/VDDCORE: U1.55 (VDDCORE); also elsewhere on the board
/~RESET: J8.10 (NRESET), R23.1, SW4.1, U1.52 (~RESET)
GNDD: C1.1, C2.1, C3.2, C4.2, C5.2, C6.1, C7.1, D1.1 (K), D2.1 (K), D3.1 (K), D4.1 (K), D5.1 (K), D6.3 (VSS), J1.19, J1.20, J1.MP1, J1.MP2, J2.19, J2.20, J2.MP1, J2.MP2, J3.19, J3.20, J3.MP1, J3.MP2, J4.2, J5.3, J5.6, J5.9, J5.12, J5.15, J5.16, J6.2, J7.2, J8.3 (GND), J8.5 (GND), SW1.1, SW2.1, SW3.1, SW4.2, U1.7 (GNDANA), U1.22 (GND), U1.33 (GND), U1.47 (GND), U1.54 (GND), U1.65 (EP), U2.4 (GND), U2.9 (EP); also elsewhere on the board
unnamed: D1.2 (A), R2.2
unnamed: D2.2 (A), R4.2
unnamed: D3.2 (A), R5.2
unnamed: D4.2 (A), R6.2
unnamed: D5.2 (A), R7.2
unnamed: F1.2, J1.1
unnamed: F2.2, J1.2
unnamed: F3.2, J2.1
unnamed: F4.2, J2.2
unnamed: F5.2, J3.1
unnamed: F6.2, J3.2
unnamed: F7.1, J5.1, J5.4, J5.7, J5.10
unnamed: J5.2, R8.2
unnamed: J5.5, R9.2
unnamed: J5.8, R10.2
unnamed: J5.11, R11.2
unnamed: F8.1, J5.13, J5.14
unnamed: R16.2, R19.1, SW1.2
unnamed: R17.2, R20.1, SW2.2
unnamed: R18.2, R21.1, SW3.2

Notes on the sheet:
I2C connector main bus out
Clock crystal with decoupling capacitors
I2C pullup resistors main bus
User adressable buttons
FFC/FPC connector 3
I2C connector for auxilary sensor
I2C connector main bus in
Mountingholes M2.5
Debug connector
2mb NOR SPI flash memory
Termination resistors USB bus
FFC/FPC connector addressable leds
Powerled and status leds
FFC/FPC connector 1
Reset button
Microchip SAMD21D microcontroller
Fiducial markings
FFC/FPC connector 2
I2C pullup resistors IO bus
WS2812B neopixel
Cload = 2 * (Ccrystal - Ctrace) = 2 * (7pF - 6pF) = 2pF Ccrystal = 7pF Cstray = 6pF

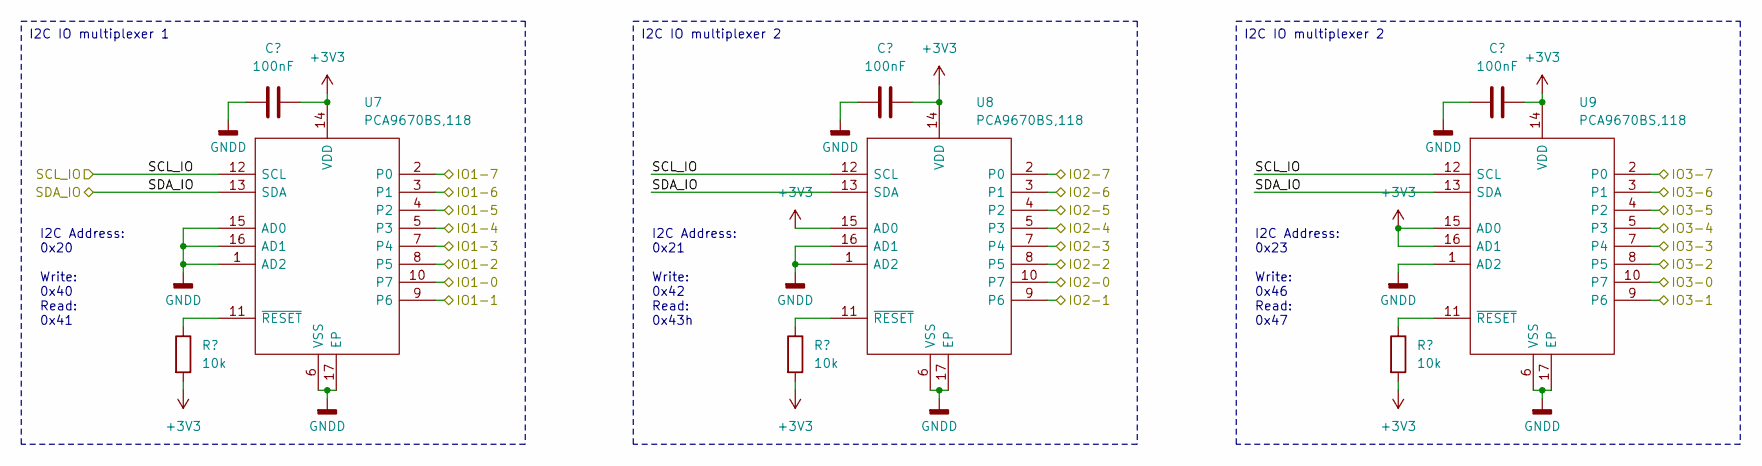
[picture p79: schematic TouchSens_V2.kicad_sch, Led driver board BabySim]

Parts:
C21: 100nF; C_0603_1608Metric_Pad1.08x0.95mm_HandSolder
R33, R34, R35: 10k; R_0603_1608Metric_Pad0.98x0.95mm_HandSolder
U7, U8, U9: PCA9670BS,118; QFN50P300X300X100-17N-D; Manufacturer_Part_Number PCA9670BS,118; Mouser Part Number 771-PCA9670BS118

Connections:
/LED1-4: U7.10 (P7); also elsewhere on the board
/LED1-5: U7.9 (P6); also elsewhere on the board
/LED1-6: U7.8 (P5); also elsewhere on the board
/LED1-7: U7.7 (P4); also elsewhere on the board
/LED1-8: U7.5 (P3); also elsewhere on the board
/LED1-9: U7.4 (P2); also elsewhere on the board
/LED1-10: U7.3 (P1); also elsewhere on the board
/LED1-11: U7.2 (P0); also elsewhere on the board
/LED2-4: U8.10 (P7); also elsewhere on the board
/LED2-5: U8.9 (P6); also elsewhere on the board
/LED2-6: U8.8 (P5); also elsewhere on the board
/LED2-7: U8.7 (P4); also elsewhere on the board
/LED2-8: U8.5 (P3); also elsewhere on the board
/LED2-9: U8.4 (P2); also elsewhere on the board
/LED2-10: U8.3 (P1); also elsewhere on the board
/LED2-11: U8.2 (P0); also elsewhere on the board
/LED3-4: U9.10 (P7); also elsewhere on the board
/LED3-5: U9.9 (P6); also elsewhere on the board
/LED3-6: U9.8 (P5); also elsewhere on the board
/LED3-7: U9.7 (P4); also elsewhere on the board
/LED3-8: U9.5 (P3); also elsewhere on the board
/LED3-9: U9.4 (P2); also elsewhere on the board
/LED3-10: U9.3 (P1); also elsewhere on the board
/LED3-11: U9.2 (P0); also elsewhere on the board
/SCL_IO: U7.12 (SCL), U8.12 (SCL), U9.12 (SCL); also elsewhere on the board
/SDA_IO: U7.13 (SDA), U8.13 (SDA), U9.13 (SDA); also elsewhere on the board
GNDD: C21.2, U7.1 (AD2), U7.6 (VSS), U7.15 (AD0), U7.16 (AD1), U7.17 (EP), U8.1 (AD2), U8.6 (VSS), U8.16 (AD1), U8.17 (EP), U9.1 (AD2), U9.6 (VSS), U9.17 (EP); also elsewhere on the board
unnamed: R33.1, U7.11 (~RESET)
unnamed: R34.1, U8.11 (~RESET)
unnamed: R35.1, U9.11 (~RESET)

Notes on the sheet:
I2C IO multiplexer 1
I2C IO multiplexer 2
I2C Address: 0x20 Write: 0x40 Read: 0x41
I2C Address: 0x23 Write: 0x46 Read: 0x47
I2C Address: 0x21 Write: 0x42 Read: 0x43h

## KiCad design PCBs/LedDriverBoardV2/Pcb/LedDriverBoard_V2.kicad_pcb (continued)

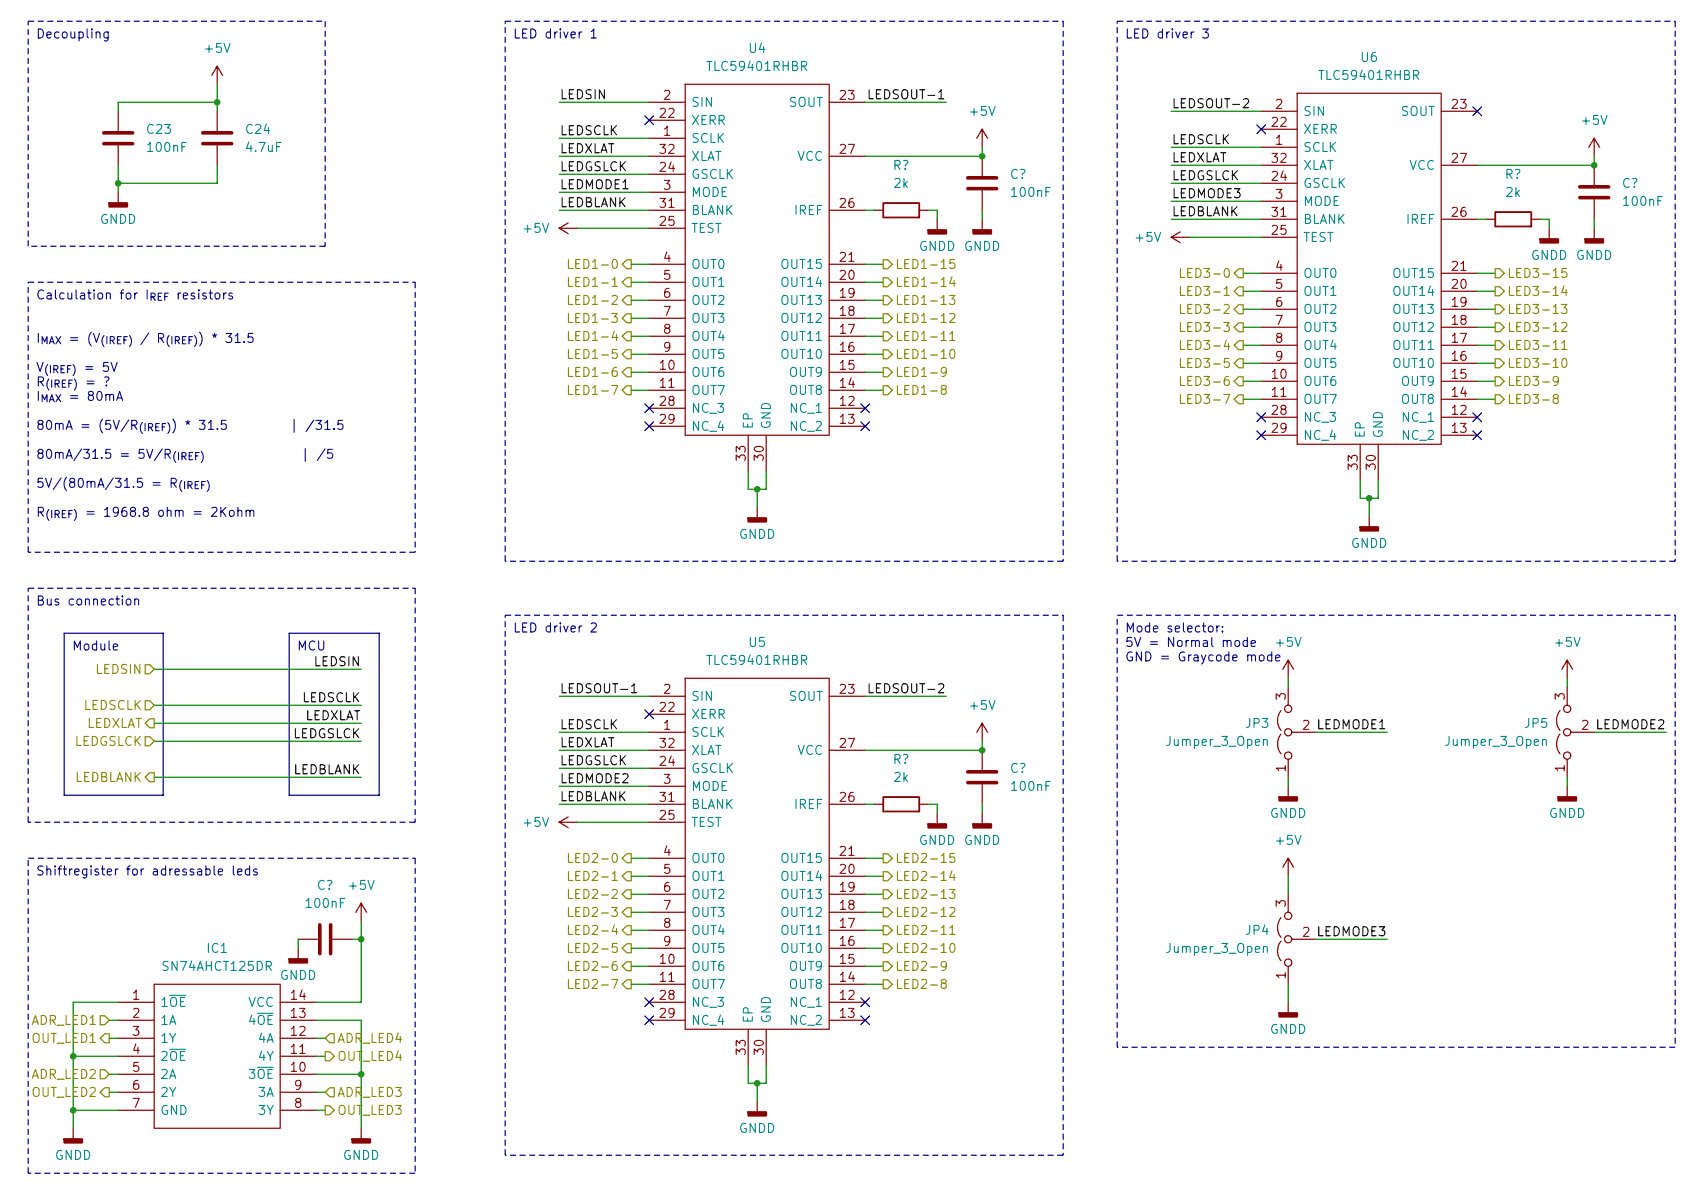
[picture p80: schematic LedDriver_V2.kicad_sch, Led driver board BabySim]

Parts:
C23, C25, C26, C27, C28: 100nF; C_0603_1608Metric_Pad1.08x0.95mm_HandSolder
C24: 4.7uF; C_0603_1608Metric_Pad1.08x0.95mm_HandSolder
IC1: SN74AHCT125DR; SOIC127P600X175-14N; Manufacturer_Part_Number SN74AHCT125DR; Mouser Part Number 595-SN74AHCT125DR
JP3, JP4, JP5: Jumper_3_Open; SolderJumper-3_P1.3mm_Open_RoundedPad1.0x1.5mm
R30, R31, R32: 2k; R_0603_1608Metric_Pad0.98x0.95mm_HandSolder
U4, U5, U6: TLC59401RHBR; QFN50P500X500X100-33N-D; Manufacturer_Part_Number TLC59401RHBR; Mouser Part Number 595-TLC59401RHBR

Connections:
+5V: C23.1, C24.1, C25.1, C26.1, C27.1, C28.1, IC1.14 (VCC), JP3.3 (B), JP4.3 (B), JP5.3 (B), U4.25 (TEST), U4.27 (VCC), U5.25 (TEST), U5.27 (VCC), U6.25 (TEST), U6.27 (VCC); also elsewhere on the board
/ADR_LED1: IC1.2 (1A); also elsewhere on the board
/ADR_LED2: IC1.5 (2A); also elsewhere on the board
/ADR_LED3: IC1.9 (3A); also elsewhere on the board
/ADR_LED4: IC1.12 (4A); also elsewhere on the board
/LED1-0: U4.4 (OUT0); also elsewhere on the board
/LED1-1: U4.5 (OUT1); also elsewhere on the board
/LED1-2: U4.6 (OUT2); also elsewhere on the board
/LED1-3: U4.7 (OUT3); also elsewhere on the board
/LED1-4: U4.8 (OUT4); also elsewhere on the board
/LED1-5: U4.9 (OUT5); also elsewhere on the board
/LED1-6: U4.10 (OUT6); also elsewhere on the board
/LED1-7: U4.11 (OUT7); also elsewhere on the board
/LED1-8: U4.14 (OUT8); also elsewhere on the board
/LED1-9: U4.15 (OUT9); also elsewhere on the board
/LED1-10: U4.16 (OUT10); also elsewhere on the board
/LED1-11: U4.17 (OUT11); also elsewhere on the board
/LED1-12: U4.18 (OUT12); also elsewhere on the board
/LED1-13: U4.19 (OUT13); also elsewhere on the board
/LED1-14: U4.20 (OUT14); also elsewhere on the board
/LED1-15: U4.21 (OUT15); also elsewhere on the board
/LED2-0: U5.4 (OUT0); also elsewhere on the board
/LED2-1: U5.5 (OUT1); also elsewhere on the board
/LED2-2: U5.6 (OUT2); also elsewhere on the board
/LED2-3: U5.7 (OUT3); also elsewhere on the board
/LED2-4: U5.8 (OUT4); also elsewhere on the board
/LED2-5: U5.9 (OUT5); also elsewhere on the board
/LED2-6: U5.10 (OUT6); also elsewhere on the board
/LED2-7: U5.11 (OUT7); also elsewhere on the board
/LED2-8: U5.14 (OUT8); also elsewhere on the board
/LED2-9: U5.15 (OUT9); also elsewhere on the board
/LED2-10: U5.16 (OUT10); also elsewhere on the board
/LED2-11: U5.17 (OUT11); also elsewhere on the board
/LED2-12: U5.18 (OUT12); also elsewhere on the board
/LED2-13: U5.19 (OUT13); also elsewhere on the board
/LED2-14: U5.20 (OUT14); also elsewhere on the board
/LED2-15: U5.21 (OUT15); also elsewhere on the board
/LED3-0: U6.4 (OUT0); also elsewhere on the board
/LED3-1: U6.5 (OUT1); also elsewhere on the board
/LED3-2: U6.6 (OUT2); also elsewhere on the board
/LED3-3: U6.7 (OUT3); also elsewhere on the board
/LED3-4: U6.8 (OUT4); also elsewhere on the board
/LED3-5: U6.9 (OUT5); also elsewhere on the board
/LED3-6: U6.10 (OUT6); also elsewhere on the board
/LED3-7: U6.11 (OUT7); also elsewhere on the board
/LED3-8: U6.14 (OUT8); also elsewhere on the board
/LED3-9: U6.15 (OUT9); also elsewhere on the board
/LED3-10: U6.16 (OUT10); also elsewhere on the board
/LED3-11: U6.17 (OUT11); also elsewhere on the board
/LED3-12: U6.18 (OUT12); also elsewhere on the board
/LED3-13: U6.19 (OUT13); also elsewhere on the board
/LED3-14: U6.20 (OUT14); also elsewhere on the board
/LED3-15: U6.21 (OUT15); also elsewhere on the board
/LEDBLANK: U4.31 (BLANK), U5.31 (BLANK), U6.31 (BLANK); also elsewhere on the board
/LEDGSLCK: U4.24 (GSCLK), U5.24 (GSCLK), U6.24 (GSCLK); also elsewhere on the board
/LEDSCLK: U4.1 (SCLK), U5.1 (SCLK), U6.1 (SCLK); also elsewhere on the board
/LEDSIN: U4.2 (SIN); also elsewhere on the board
/LEDXLAT: U4.32 (XLAT), U5.32 (XLAT), U6.32 (XLAT); also elsewhere on the board
/LedDriver/LEDMODE1: JP3.2 (C), U4.3 (MODE)
/LedDriver/LEDMODE2: JP5.2 (C), U5.3 (MODE)
/LedDriver/LEDMODE3: JP4.2 (C), U6.3 (MODE)
/LedDriver/LEDSOUT-1: U4.23 (SOUT), U5.2 (SIN)
/LedDriver/LEDSOUT-2: U5.23 (SOUT), U6.2 (SIN)
/OUT_LED1: IC1.3 (1Y); also elsewhere on the board
/OUT_LED2: IC1.6 (2Y); also elsewhere on the board
/OUT_LED3: IC1.8 (3Y); also elsewhere on the board
/OUT_LED4: IC1.11 (4Y); also elsewhere on the board
GNDD: C23.2, C24.2, C25.2, C26.2, C27.2, C28.2, IC1.1 (1~OE), IC1.4 (2~OE), IC1.7 (GND), IC1.10 (3~OE), IC1.13 (4~OE), JP3.1 (A), JP4.1 (A), JP5.1 (A), R30.2, R31.2, R32.2, U4.30 (GND), U4.33 (EP), U5.30 (GND), U5.33 (EP), U6.30 (GND), U6.33 (EP); also elsewhere on the board
unnamed: R30.1, U4.26 (IREF)
unnamed: R31.1, U5.26 (IREF)
unnamed: R32.1, U6.26 (IREF)

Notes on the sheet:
Bus connection
Calculation for I_{REF} resistors I_{MAX} = (V_{(IREF)} / R_{(IREF)}) * 31.5 V_{(IREF)} = 5V R_{(IREF)} = ? I_{MAX} = 80mA 80mA = (5V/R_{(IREF)}) * 31.5 | /31.5 80mA/31.5 = 5V/R_{(IREF)} | /5 5V/(80mA/31.5 = R_{(IREF)} R_{(IREF)} = 1968.8 ohm = 2Kohm
Module
LED driver 3
Shiftregister for adressable leds
LED driver 2
MCU
Decoupling
LED driver 1
Mode selector: 5V = Normal mode GND = Graycode mode

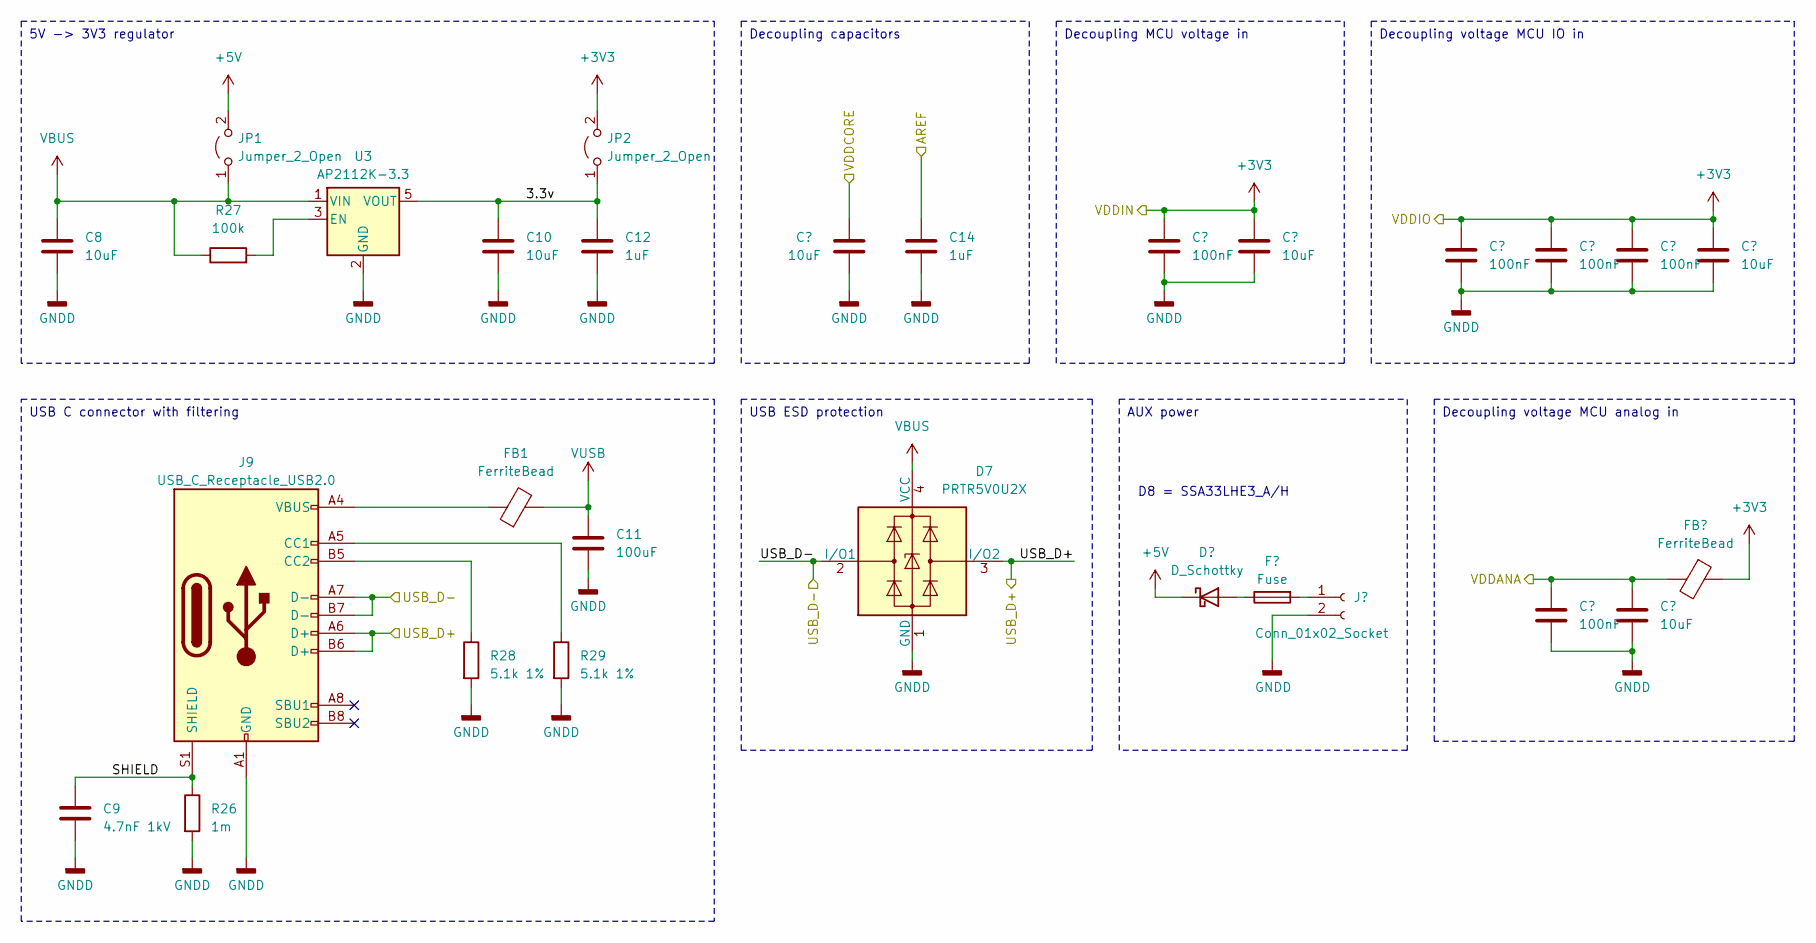
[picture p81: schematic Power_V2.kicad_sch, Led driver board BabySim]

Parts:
C8, C10: 10uF; C_1206_3216Metric_Pad1.33x1.80mm_HandSolder
C9: 4.7nF 1kV; C_0805_2012Metric_Pad1.18x1.45mm_HandSolder
C11: 100uF; C_0805_2012Metric_Pad1.18x1.45mm_HandSolder
C12: 1uF; C_1206_3216Metric_Pad1.33x1.80mm_HandSolder
C13, C16, C21, C22: 10uF; C_0603_1608Metric_Pad1.08x0.95mm_HandSolder
C14: 1uF; C_0603_1608Metric_Pad1.08x0.95mm_HandSolder
C15, C17, C18, C19, C20: 100nF; C_0603_1608Metric_Pad1.08x0.95mm_HandSolder
D7: PRTR5V0U2X; SOT-143
D8: D_Schottky; DIOM5127X229N
F9: Fuse; 0031.7701.11
FB1, FB2: FerriteBead; L_0805_2012Metric_Pad1.15x1.40mm_HandSolder
J9: USB_C_Receptacle_USB2.0; USB_C_Receptacle_HRO_TYPE-C-31-M-12
J10: Conn_01x02_Socket; TerminalBlock_Phoenix_PT-1,5-2-3.5-H_1x02_P3.50mm_Horizontal
JP1, JP2: Jumper_2_Open; SolderJumper-2_P1.3mm_Open_RoundedPad1.0x1.5mm
R26: 1m; R_0603_1608Metric_Pad0.98x0.95mm_HandSolder
R27: 100k; R_0603_1608Metric_Pad0.98x0.95mm_HandSolder
R28, R29: 5.1k 1%; R_0603_1608Metric_Pad0.98x0.95mm_HandSolder
U3: AP2112K-3.3; SOT-23-5

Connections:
+5V: D8.1 (K), JP1.2 (B); also elsewhere on the board
/AREF: C14.1; also elsewhere on the board
/Power/3.3v: C10.1, C12.1, JP2.1 (A), U3.5 (VOUT)
/Power/SHIELD: C9.1, J9.S1 (SHIELD), R26.1
/USB_D+: D7.3 (I/O2), J9.A6 (D+), J9.B6 (D+); also elsewhere on the board
/USB_D-: D7.2 (I/O1), J9.A7 (D-), J9.B7 (D-); also elsewhere on the board
/VDDCORE: C13.2; also elsewhere on the board
GNDD: C8.2, C9.2, C10.2, C11.2, C12.2, C13.1, C14.2, C15.2, C16.2, C17.2, C18.2, C19.2, C20.2, C21.2, C22.2, D7.1 (GND), J9.A1 (GND), J9.A12 (GND), J9.B1 (GND), J9.B12 (GND), J10.2, R26.2, R28.2, R29.2, U3.2 (GND); also elsewhere on the board
unnamed: D8.2 (A), F9.1
unnamed: FB1.1, J9.A4 (VBUS), J9.A9 (VBUS), J9.B4 (VBUS), J9.B9 (VBUS)
unnamed: J9.A5 (CC1), R29.1
unnamed: J9.B5 (CC2), R28.1
unnamed: F9.2, J10.1
unnamed: R27.2, U3.3 (EN)
VBUS: C8.1, C11.1, D7.4 (VCC), FB1.2, JP1.1 (A), R27.1, U3.1 (VIN)

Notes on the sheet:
AUX power
Decoupling voltage MCU analog in
5V -> 3V3 regulator
Decoupling MCU voltage in
USB ESD protection
Decoupling capacitors
USB C connector with filtering
Decoupling voltage MCU IO in
D8 = SSA33LHE3_A/H

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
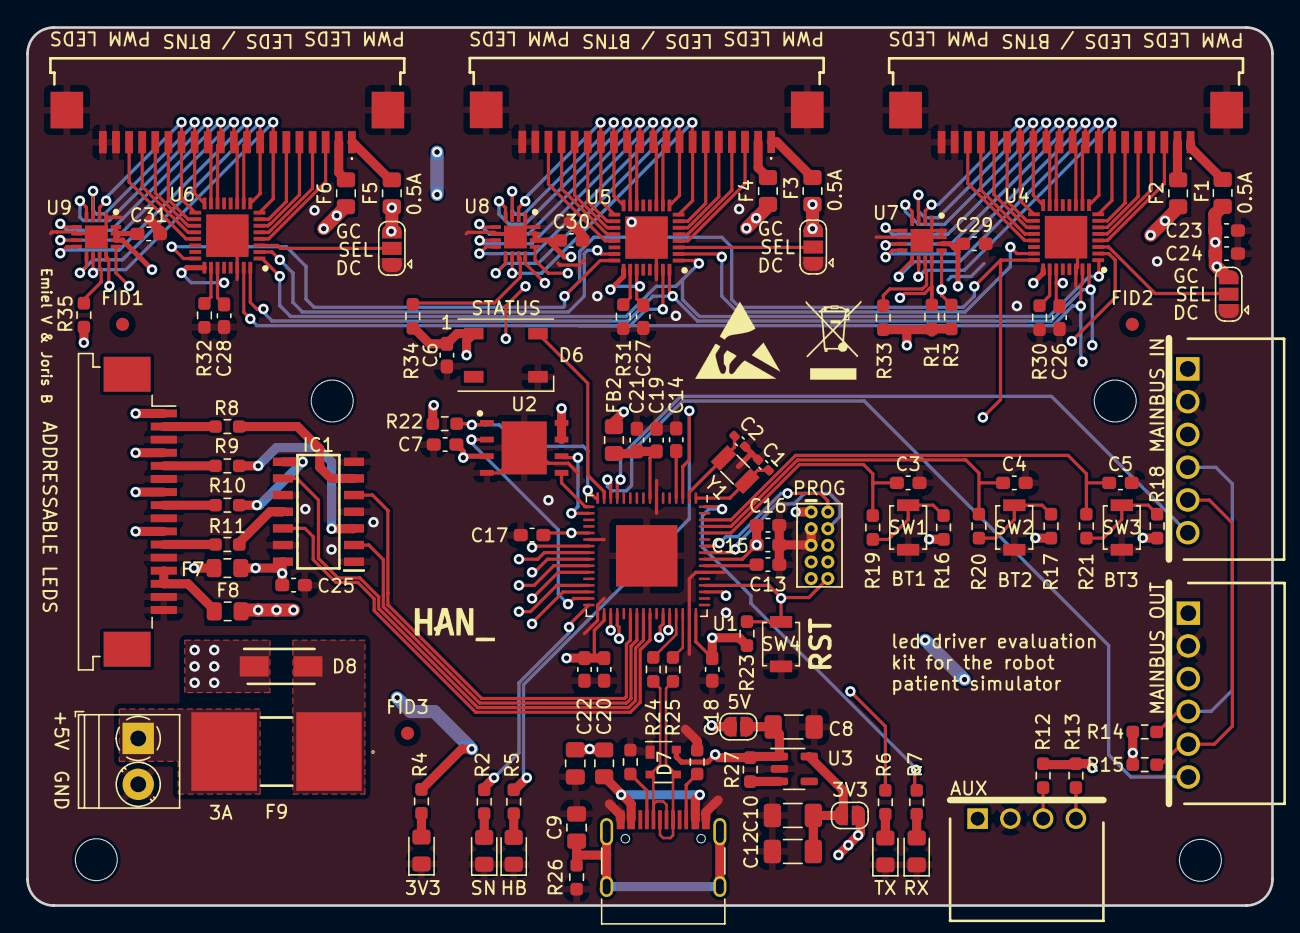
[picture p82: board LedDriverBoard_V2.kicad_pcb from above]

Board: 4 copper layers, 95.0 x 67.0 mm, 122 parts (0 on the bottom side), 136 nets.

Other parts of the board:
C29, C30, C31: 100nF; C_0603_1608Metric_Pad1.08x0.95mm_HandSolder

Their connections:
GNDD: C29.2, C30.2, C31.2; also elsewhere on the board

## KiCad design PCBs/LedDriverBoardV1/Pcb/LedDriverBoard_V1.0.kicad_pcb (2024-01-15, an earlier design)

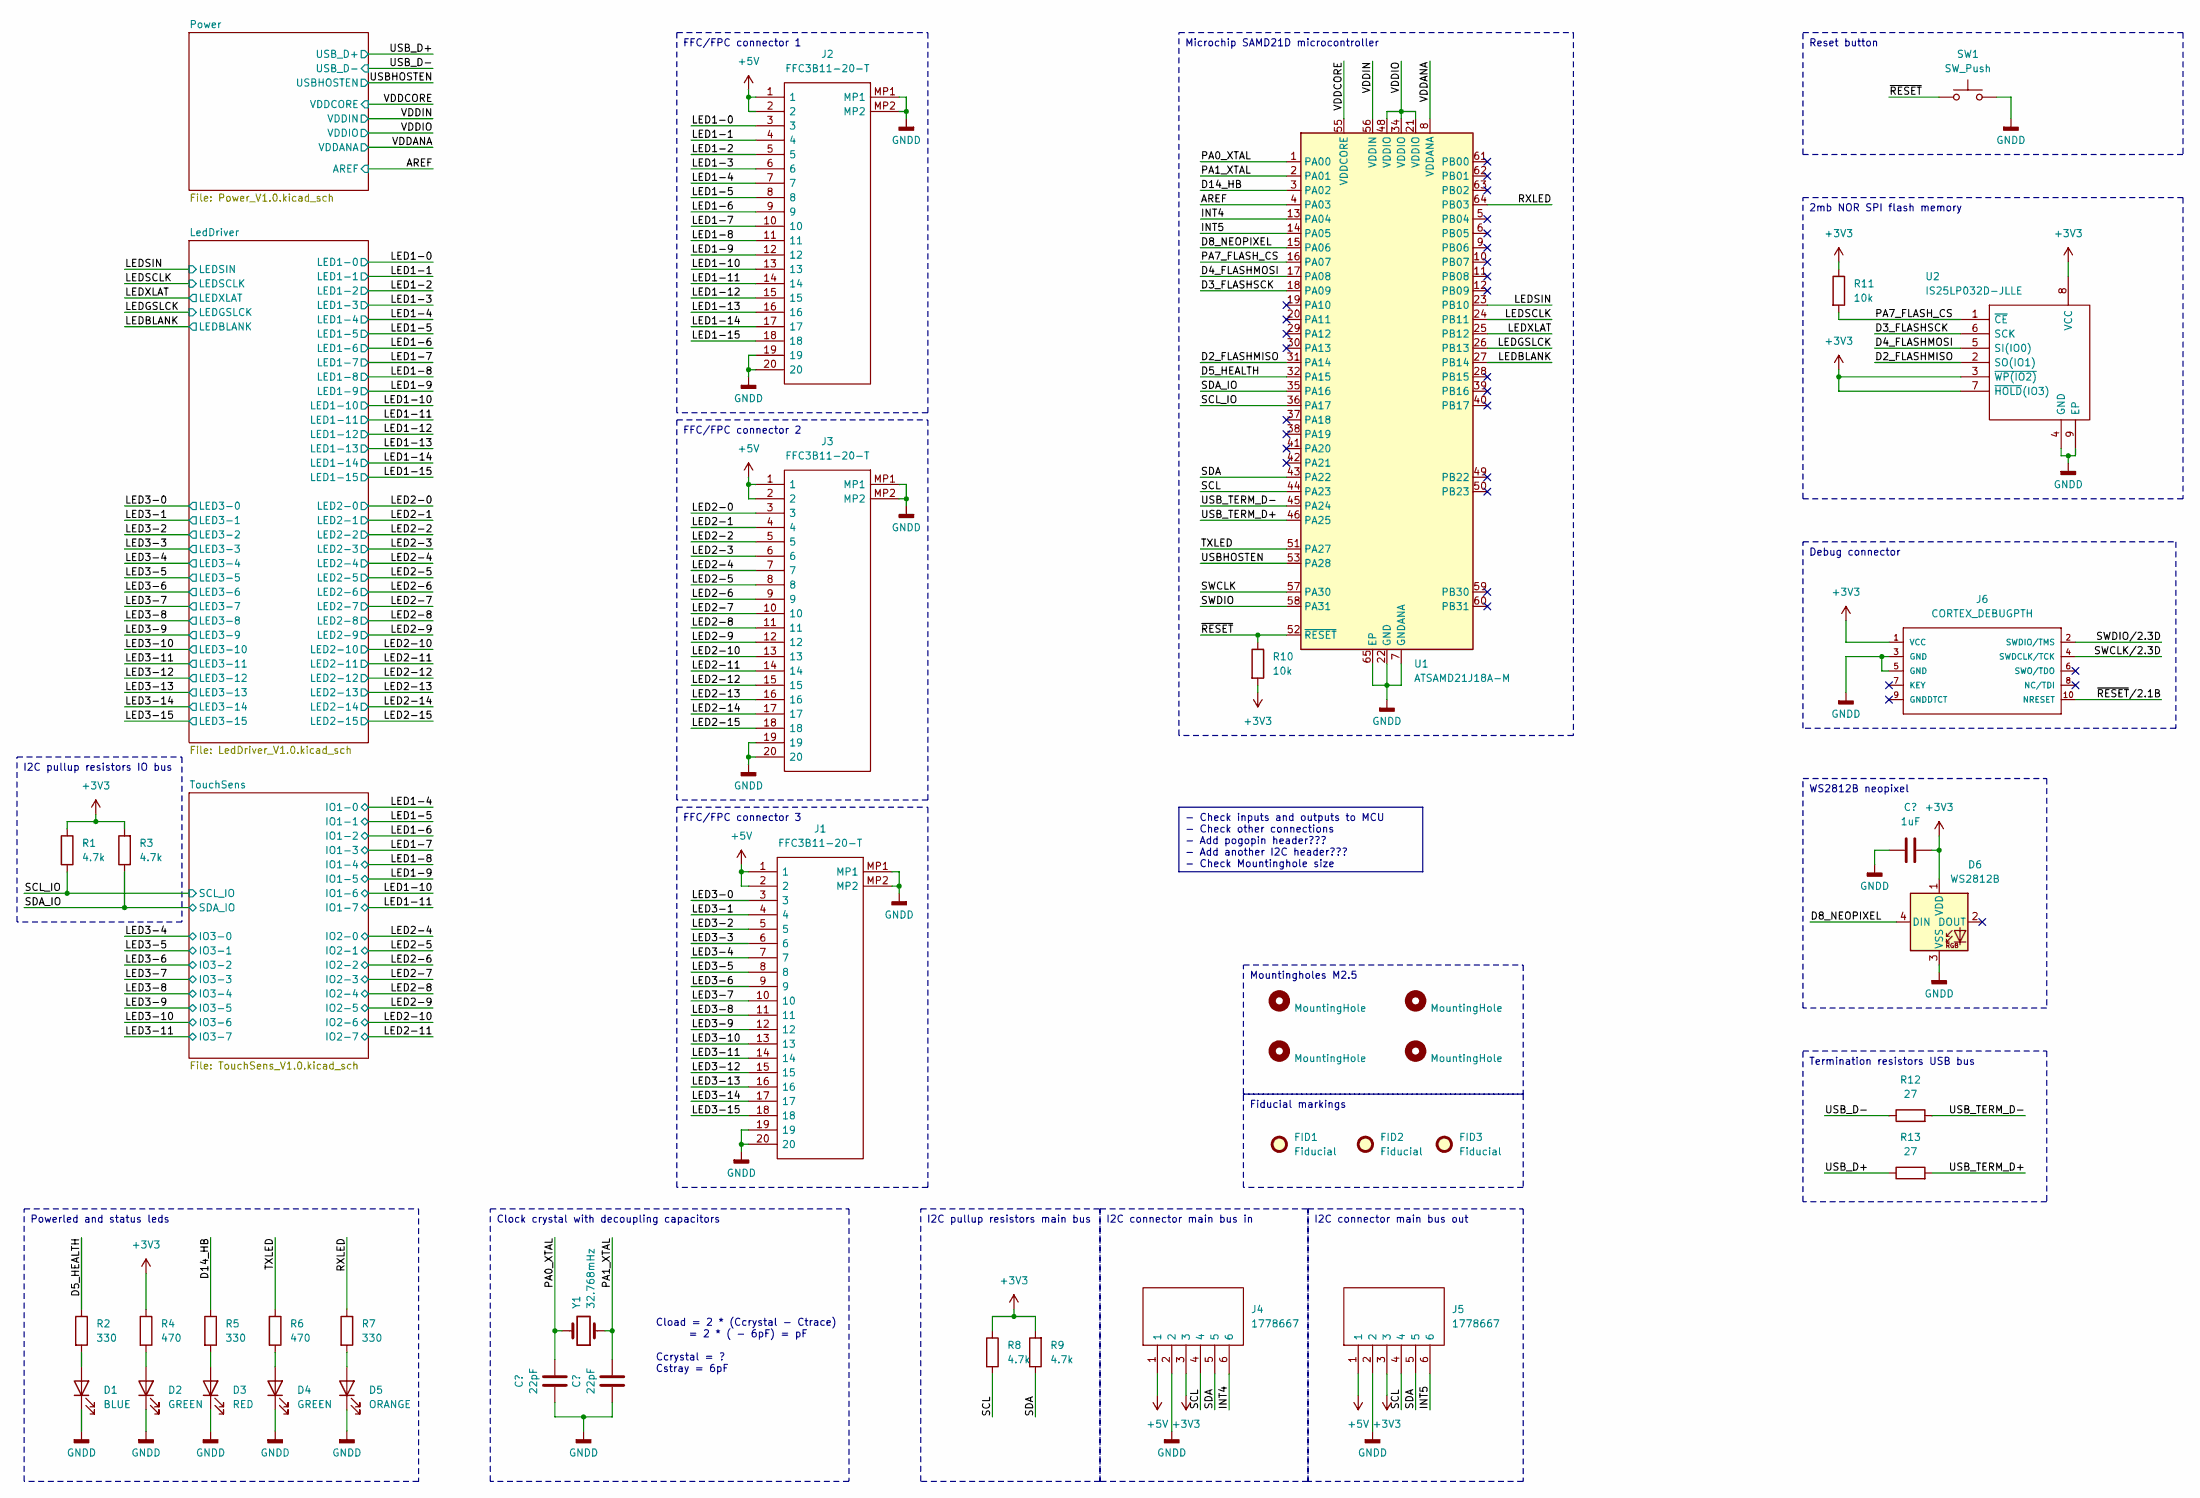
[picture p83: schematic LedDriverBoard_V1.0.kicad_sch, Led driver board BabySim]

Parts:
C1, C2: 22pF; C_0402_1005Metric_Pad0.74x0.62mm_HandSolder
C3: 1uF; C_0603_1608Metric_Pad1.08x0.95mm_HandSolder
D1: BLUE; LED_0805_2012Metric_Pad1.15x1.40mm_HandSolder
D2, D4: GREEN; LED_0805_2012Metric_Pad1.15x1.40mm_HandSolder
D3: RED; LED_0805_2012Metric_Pad1.15x1.40mm_HandSolder
D5: ORANGE; LED_0805_2012Metric_Pad1.15x1.40mm_HandSolder
D6: WS2812B; LED_WS2812B_PLCC4_5.0x5.0mm_P3.2mm
FID1, FID2, FID3: Fiducial; Fiducial_1mm_Mask2mm
H1, H2, H3, H4: MountingHole; MountingHole_2.7mm_M2.5_DIN965
J1, J2, J3: FFC3B11-20-T; FFC3B1120T; Manufacturer_Part_Number FFC3B11-20-T; Mouser Part Number 640-FFC3B11-20-T
J4, J5: 1778667; SHDRRA6W70P0X250_1X6_1670X750X510P; Manufacturer_Part_Number 1778667; Mouser Part Number 651-1778667
J6: CORTEX_DEBUGPTH; 2X5-PTH-1.27MM
R1, R3, R8, R9: 4.7k; R_0603_1608Metric_Pad0.98x0.95mm_HandSolder
R2, R5, R7: 330; R_0603_1608Metric_Pad0.98x0.95mm_HandSolder
R4, R6: 470; R_0603_1608Metric_Pad0.98x0.95mm_HandSolder
R10, R11: 10k; R_0603_1608Metric_Pad0.98x0.95mm_HandSolder
R12, R13: 27; R_0603_1608Metric_Pad0.98x0.95mm_HandSolder
SW1: SW_Push; PTS810SJG250SMTRLFS
U1: ATSAMD21J18A-M; QFN-64-1EP_9x9mm_P0.5mm_EP4.7x4.7mm
U2: IS25LP032D-JLLE; SON127P600X500X75-9N-D; Manufacturer_Part_Number IS25LP032D-JLLE; Mouser Part Number 870-IS25LP032D-JLLE
Y1: 32.768mHz; Crystal_SMD_3215-2Pin_3.2x1.5mm

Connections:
+3V3: C3.2, D6.1 (VDD), J4.3, J5.3, J6.1 (VCC), R1.1, R3.2, R4.1, R8.1, R9.2, R10.2, R11.1, U1.21 (VDDIO), U1.34 (VDDIO), U1.48 (VDDIO), U1.56 (VDDIN), U2.3 (~WP(IO2)), U2.7 (~HOLD(IO3)), U2.8 (VCC); also elsewhere on the board
+5V: J1.1, J1.2, J2.1, J2.2, J3.1, J3.2, J4.1, J5.1; also elsewhere on the board
/AREF: U1.4 (PA03); also elsewhere on the board
/D2_FLASHMISO: U1.31 (PA14), U2.2 (SO(IO1))
/D3_FLASHSCK: U1.18 (PA09), U2.6 (SCK)
/D4_FLASHMOSI: U1.17 (PA08), U2.5 (SI(IO0))
/D5_HEALTH: R2.1, U1.32 (PA15)
/D8_NEOPIXEL: D6.4 (DIN), U1.15 (PA06)
/D14_HB: R5.1, U1.3 (PA02)
/INT4: J4.6, U1.13 (PA04)
/INT5: J5.6, U1.14 (PA05)
/LED1-0: J2.3; also elsewhere on the board
/LED1-1: J2.4; also elsewhere on the board
/LED1-2: J2.5; also elsewhere on the board
/LED1-3: J2.6; also elsewhere on the board
/LED1-4: J2.7; also elsewhere on the board
/LED1-5: J2.8; also elsewhere on the board
/LED1-6: J2.9; also elsewhere on the board
/LED1-7: J2.10; also elsewhere on the board
/LED1-8: J2.11; also elsewhere on the board
/LED1-9: J2.12; also elsewhere on the board
/LED1-10: J2.13; also elsewhere on the board
/LED1-11: J2.14; also elsewhere on the board
/LED1-12: J2.15; also elsewhere on the board
/LED1-13: J2.16; also elsewhere on the board
/LED1-14: J2.17; also elsewhere on the board
/LED1-15: J2.18; also elsewhere on the board
/LED2-0: J3.3; also elsewhere on the board
/LED2-1: J3.4; also elsewhere on the board
/LED2-2: J3.5; also elsewhere on the board
/LED2-3: J3.6; also elsewhere on the board
/LED2-4: J3.7; also elsewhere on the board
/LED2-5: J3.8; also elsewhere on the board
/LED2-6: J3.9; also elsewhere on the board
/LED2-7: J3.10; also elsewhere on the board
/LED2-8: J3.11; also elsewhere on the board
/LED2-9: J3.12; also elsewhere on the board
/LED2-10: J3.13; also elsewhere on the board
/LED2-11: J3.14; also elsewhere on the board
/LED2-12: J3.15; also elsewhere on the board
/LED2-13: J3.16; also elsewhere on the board
/LED2-14: J3.17; also elsewhere on the board
/LED2-15: J3.18; also elsewhere on the board
/LED3-0: J1.3; also elsewhere on the board
/LED3-1: J1.4; also elsewhere on the board
/LED3-2: J1.5; also elsewhere on the board
/LED3-3: J1.6; also elsewhere on the board
/LED3-4: J1.7; also elsewhere on the board
/LED3-5: J1.8; also elsewhere on the board
/LED3-6: J1.9; also elsewhere on the board
/LED3-7: J1.10; also elsewhere on the board
/LED3-8: J1.11; also elsewhere on the board
/LED3-9: J1.12; also elsewhere on the board
/LED3-10: J1.13; also elsewhere on the board
/LED3-11: J1.14; also elsewhere on the board
/LED3-12: J1.15; also elsewhere on the board
/LED3-13: J1.16; also elsewhere on the board
/LED3-14: J1.17; also elsewhere on the board
/LED3-15: J1.18; also elsewhere on the board
/LEDBLANK: U1.27 (PB14); also elsewhere on the board
/LEDGSLCK: U1.26 (PB13); also elsewhere on the board
/LEDSCLK: U1.24 (PB11); also elsewhere on the board
/LEDSIN: U1.23 (PB10); also elsewhere on the board
/LEDXLAT: U1.25 (PB12); also elsewhere on the board
/PA0_XTAL: C1.2, U1.1 (PA00), Y1.2
/PA1_XTAL: C2.2, U1.2 (PA01), Y1.1
/PA7_FLASH_CS: R11.2, U1.16 (PA07), U2.1 (~CE)
/RXLED: R7.1, U1.64 (PB03)
/SCL: J4.4, J5.4, R8.2, U1.44 (PA23)
/SCL_IO: R1.2, U1.36 (PA17); also elsewhere on the board
/SDA: J4.5, J5.5, R9.1, U1.43 (PA22)
/SDA_IO: R3.1, U1.35 (PA16); also elsewhere on the board
/SWCLK: U1.57 (PA30)
/SWCLK/2.3D: J6.4 (SWDCLK/TCK)
/SWDIO: U1.58 (PA31)
/SWDIO/2.3D: J6.2 (SWDIO/TMS)
/TXLED: R6.1, U1.51 (PA27)
/USBHOSTEN: U1.53 (PA28); also elsewhere on the board
/USB_D+: R13.1; also elsewhere on the board
/USB_D-: R12.1; also elsewhere on the board
/USB_TERM_D+: R13.2, U1.46 (PA25)
/USB_TERM_D-: R12.2, U1.45 (PA24)
/VDDANA: U1.8 (VDDANA); also elsewhere on the board
/VDDCORE: U1.55 (VDDCORE); also elsewhere on the board
/~RESET: R10.1, SW1.1, U1.52 (~RESET)
/~RESET/2.1B: J6.10 (NRESET)
GNDD: C1.1, C2.1, C3.1, D1.1 (K), D2.1 (K), D3.1 (K), D4.1 (K), D5.1 (K), D6.3 (VSS), J1.19, J1.20, J1.MP1, J1.MP2, J2.19, J2.20, J2.MP1, J2.MP2, J3.19, J3.20, J3.MP1, J3.MP2, J4.2, J5.2, J6.3 (GND), J6.5 (GND), SW1.2, U1.7 (GNDANA), U1.22 (GND), U1.33 (GND), U1.47 (GND), U1.54 (GND), U1.65 (EP), U2.4 (GND), U2.9 (EP); also elsewhere on the board
unnamed: D1.2 (A), R2.2
unnamed: D2.2 (A), R4.2
unnamed: D3.2 (A), R5.2
unnamed: D4.2 (A), R6.2
unnamed: D5.2 (A), R7.2

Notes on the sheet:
I2C connector main bus out
Clock crystal with decoupling capacitors
I2C pullup resistors main bus
FFC/FPC connector 3
I2C connector main bus in
Mountingholes M2.5
Debug connector
2mb NOR SPI flash memory
- Check inputs and outputs to MCU - Check other connections - Add pogopin header??? - Add another I2C header??? - Check Mountinghole size
Termination resistors USB bus
Powerled and status leds
FFC/FPC connector 1
Reset button
Microchip SAMD21D microcontroller
Fiducial markings
FFC/FPC connector 2
I2C pullup resistors IO bus
WS2812B neopixel
Cload = 2 * (Ccrystal - Ctrace) = 2 * ( - 6pF) = pF Ccrystal = ? Cstray = 6pF

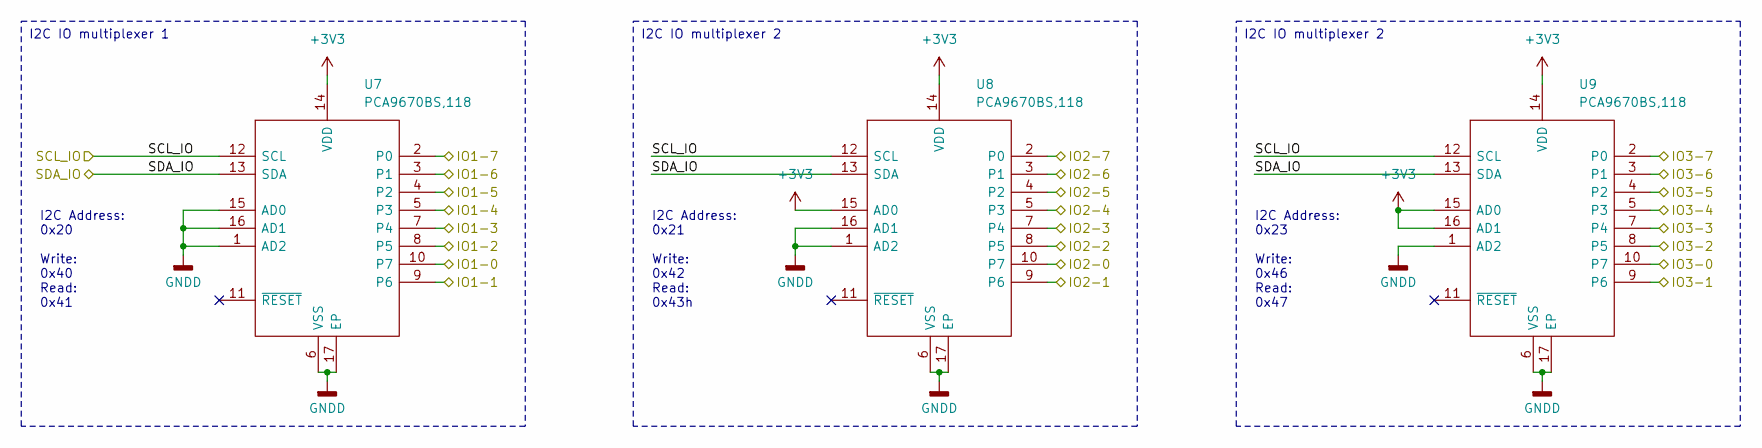
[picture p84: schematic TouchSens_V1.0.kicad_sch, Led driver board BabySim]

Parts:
U7, U8, U9: PCA9670BS,118; QFN50P300X300X100-17N-D; Manufacturer_Part_Number PCA9670BS,118; Mouser Part Number 771-PCA9670BS118

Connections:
+3V3: U7.14 (VDD), U8.14 (VDD), U8.15 (AD0), U9.14 (VDD), U9.15 (AD0), U9.16 (AD1); also elsewhere on the board
/LED1-4: U7.10 (P7); also elsewhere on the board
/LED1-5: U7.9 (P6); also elsewhere on the board
/LED1-6: U7.8 (P5); also elsewhere on the board
/LED1-7: U7.7 (P4); also elsewhere on the board
/LED1-8: U7.5 (P3); also elsewhere on the board
/LED1-9: U7.4 (P2); also elsewhere on the board
/LED1-10: U7.3 (P1); also elsewhere on the board
/LED1-11: U7.2 (P0); also elsewhere on the board
/LED2-4: U8.10 (P7); also elsewhere on the board
/LED2-5: U8.9 (P6); also elsewhere on the board
/LED2-6: U8.8 (P5); also elsewhere on the board
/LED2-7: U8.7 (P4); also elsewhere on the board
/LED2-8: U8.5 (P3); also elsewhere on the board
/LED2-9: U8.4 (P2); also elsewhere on the board
/LED2-10: U8.3 (P1); also elsewhere on the board
/LED2-11: U8.2 (P0); also elsewhere on the board
/LED3-4: U9.10 (P7); also elsewhere on the board
/LED3-5: U9.9 (P6); also elsewhere on the board
/LED3-6: U9.8 (P5); also elsewhere on the board
/LED3-7: U9.7 (P4); also elsewhere on the board
/LED3-8: U9.5 (P3); also elsewhere on the board
/LED3-9: U9.4 (P2); also elsewhere on the board
/LED3-10: U9.3 (P1); also elsewhere on the board
/LED3-11: U9.2 (P0); also elsewhere on the board
/SCL_IO: U7.12 (SCL), U8.12 (SCL), U9.12 (SCL); also elsewhere on the board
/SDA_IO: U7.13 (SDA), U8.13 (SDA), U9.13 (SDA); also elsewhere on the board
GNDD: U7.1 (AD2), U7.6 (VSS), U7.15 (AD0), U7.16 (AD1), U7.17 (EP), U8.1 (AD2), U8.6 (VSS), U8.16 (AD1), U8.17 (EP), U9.1 (AD2), U9.6 (VSS), U9.17 (EP); also elsewhere on the board

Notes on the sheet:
I2C IO multiplexer 1
I2C IO multiplexer 2
I2C Address: 0x20 Write: 0x40 Read: 0x41
I2C Address: 0x23 Write: 0x46 Read: 0x47
I2C Address: 0x21 Write: 0x42 Read: 0x43h


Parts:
C19, C21, C22, C23: 100nF; C_0603_1608Metric_Pad1.08x0.95mm_HandSolder
C20: 4.7uF; C_0603_1608Metric_Pad1.08x0.95mm_HandSolder
JP3: Jumper_3_Bridged12; SolderJumper-3_P1.3mm_Bridged2Bar12_RoundedPad1.0x1.5mm
R16, R17, R18: 2k; R_0603_1608Metric_Pad0.98x0.95mm_HandSolder
U4, U5, U6: TLC59401RHBR; QFN50P500X500X100-33N-D; Manufacturer_Part_Number TLC59401RHBR; Mouser Part Number 595-TLC59401RHBR

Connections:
+5V: C19.1, C20.1, C21.1, C22.1, C23.1, JP3.3 (B), U4.25 (TEST), U4.27 (VCC), U5.25 (TEST), U5.27 (VCC), U6.25 (TEST), U6.27 (VCC); also elsewhere on the board
/LED1-0: U4.4 (OUT0); also elsewhere on the board
/LED1-1: U4.5 (OUT1); also elsewhere on the board
/LED1-2: U4.6 (OUT2); also elsewhere on the board
/LED1-3: U4.7 (OUT3); also elsewhere on the board
/LED1-4: U4.8 (OUT4); also elsewhere on the board
/LED1-5: U4.9 (OUT5); also elsewhere on the board
/LED1-6: U4.10 (OUT6); also elsewhere on the board
/LED1-7: U4.11 (OUT7); also elsewhere on the board
/LED1-8: U4.14 (OUT8); also elsewhere on the board
/LED1-9: U4.15 (OUT9); also elsewhere on the board
/LED1-10: U4.16 (OUT10); also elsewhere on the board
/LED1-11: U4.17 (OUT11); also elsewhere on the board
/LED1-12: U4.18 (OUT12); also elsewhere on the board
/LED1-13: U4.19 (OUT13); also elsewhere on the board
/LED1-14: U4.20 (OUT14); also elsewhere on the board
/LED1-15: U4.21 (OUT15); also elsewhere on the board
/LED2-0: U5.4 (OUT0); also elsewhere on the board
/LED2-1: U5.5 (OUT1); also elsewhere on the board
/LED2-2: U5.6 (OUT2); also elsewhere on the board
/LED2-3: U5.7 (OUT3); also elsewhere on the board
/LED2-4: U5.8 (OUT4); also elsewhere on the board
/LED2-5: U5.9 (OUT5); also elsewhere on the board
/LED2-6: U5.10 (OUT6); also elsewhere on the board
/LED2-7: U5.11 (OUT7); also elsewhere on the board
/LED2-8: U5.14 (OUT8); also elsewhere on the board
/LED2-9: U5.15 (OUT9); also elsewhere on the board
/LED2-10: U5.16 (OUT10); also elsewhere on the board
/LED2-11: U5.17 (OUT11); also elsewhere on the board
/LED2-12: U5.18 (OUT12); also elsewhere on the board
/LED2-13: U5.19 (OUT13); also elsewhere on the board
/LED2-14: U5.20 (OUT14); also elsewhere on the board
/LED2-15: U5.21 (OUT15); also elsewhere on the board
/LED3-0: U6.4 (OUT0); also elsewhere on the board
/LED3-1: U6.5 (OUT1); also elsewhere on the board
/LED3-2: U6.6 (OUT2); also elsewhere on the board
/LED3-3: U6.7 (OUT3); also elsewhere on the board
/LED3-4: U6.8 (OUT4); also elsewhere on the board
/LED3-5: U6.9 (OUT5); also elsewhere on the board
/LED3-6: U6.10 (OUT6); also elsewhere on the board
/LED3-7: U6.11 (OUT7); also elsewhere on the board
/LED3-8: U6.14 (OUT8); also elsewhere on the board
/LED3-9: U6.15 (OUT9); also elsewhere on the board
/LED3-10: U6.16 (OUT10); also elsewhere on the board
/LED3-11: U6.17 (OUT11); also elsewhere on the board
/LED3-12: U6.18 (OUT12); also elsewhere on the board
/LED3-13: U6.19 (OUT13); also elsewhere on the board
/LED3-14: U6.20 (OUT14); also elsewhere on the board
/LED3-15: U6.21 (OUT15); also elsewhere on the board
/LEDBLANK: U4.31 (BLANK), U5.31 (BLANK), U6.31 (BLANK); also elsewhere on the board
/LEDGSLCK: U4.24 (GSCLK), U5.24 (GSCLK), U6.24 (GSCLK); also elsewhere on the board
/LEDSCLK: U4.1 (SCLK), U5.1 (SCLK), U6.1 (SCLK); also elsewhere on the board
/LEDSIN: U4.2 (SIN); also elsewhere on the board
/LEDXLAT: U4.32 (XLAT), U5.32 (XLAT), U6.32 (XLAT); also elsewhere on the board
/LedDriver/LEDMODE: JP3.2 (C), U4.3 (MODE), U5.3 (MODE), U6.3 (MODE)
/LedDriver/LEDSOUT-1: U4.23 (SOUT), U5.2 (SIN)
/LedDriver/LEDSOUT-2: U5.23 (SOUT), U6.2 (SIN)
GNDD: C19.2, C20.2, C21.2, C22.2, C23.2, JP3.1 (A), R16.2, R17.2, R18.2, U4.30 (GND), U4.33 (EP), U5.30 (GND), U5.33 (EP), U6.30 (GND), U6.33 (EP); also elsewhere on the board
unnamed: R16.1, U4.26 (IREF)
unnamed: R17.1, U5.26 (IREF)
unnamed: R18.1, U6.26 (IREF)

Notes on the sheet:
Bus connection
Calculation for I_{REF} resistors
Module
LED driver 3
LED driver 2
MCU
Decoupling
LED driver 1
Mode selector: 5V = Graycode mode GND = Normal mode
I_{MAX} = (V_{(IREF)} / R_{(IREF)}) * 31.5 V_{(IREF)} = 5V R_{(IREF)} = ? I_{MAX} = 80mA 80mA = (5V/R_{(IREF)}) * 31.5 | /31.5 80mA/31.5 = 5V/R_{(IREF)} | /5 5V/(80mA/31.5 = R_{(IREF)} R_{(IREF)} = 1968.8 ohm = 2Kohm

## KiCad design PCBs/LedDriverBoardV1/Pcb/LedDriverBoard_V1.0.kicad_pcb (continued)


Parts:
C4, C7: 10uF; C_1206_3216Metric_Pad1.33x1.80mm_HandSolder
C5: 4.7nF 1kV; C_0805_2012Metric_Pad1.18x1.45mm_HandSolder
C6: 100uF; C_0603_1608Metric_Pad1.08x0.95mm_HandSolder
C8: 1uF; C_1206_3216Metric_Pad1.33x1.80mm_HandSolder
C9, C12, C17, C18: 10uF; C_0603_1608Metric_Pad1.08x0.95mm_HandSolder
C10: 1uF; C_0603_1608Metric_Pad1.08x0.95mm_HandSolder
C11, C13, C14, C15, C16: 100nF; C_0603_1608Metric_Pad1.08x0.95mm_HandSolder
D7: PRTR5V0U2X; SOT-143
D8: ESD9B5.0ST5G; D_SOD-923
FB1, FB2: FerriteBead; L_0805_2012Metric_Pad1.15x1.40mm_HandSolder
J7: USB_B_Mini; USB_Micro-B_Amphenol_10103594-0001LF_Horizontal
JP1, JP2: Jumper_2_Open; SolderJumper-2_P1.3mm_Open_RoundedPad1.0x1.5mm
R14: 1M; R_0603_1608Metric_Pad0.98x0.95mm_HandSolder
R15: 100k; R_0603_1608Metric_Pad0.98x0.95mm_HandSolder
U3: AP2112K-3.3; SOT-23-5

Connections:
+3V3: C11.1, C12.1, C13.1, C14.1, C16.1, C18.1, FB2.1, JP2.2 (B); also elsewhere on the board
+5V: JP1.2 (B); also elsewhere on the board
/AREF: C10.1; also elsewhere on the board
/Power/3.3v: C7.1, C8.1, JP2.1 (A), U3.5 (VOUT)
/Power/SHIELD: C5.1, J7.6 (Shield), R14.1
/USBHOSTEN: D8.2 (A2), J7.4 (ID); also elsewhere on the board
/USB_D+: D7.3 (I/O2), J7.3 (D+); also elsewhere on the board
/USB_D-: D7.2 (I/O1), J7.2 (D-); also elsewhere on the board
/VDDANA: C15.1, C17.1, FB2.2; also elsewhere on the board
/VDDCORE: C9.2; also elsewhere on the board
GNDD: C4.2, C5.2, C6.2, C7.2, C8.2, C9.1, C10.2, C11.2, C12.2, C13.2, C14.2, C15.2, C16.2, C17.2, C18.2, D7.1 (GND), D8.1 (A1), J7.5 (GND), R14.2, U3.2 (GND); also elsewhere on the board
unnamed: FB1.1, J7.1 (VBUS)
unnamed: R15.2, U3.3 (EN)
VBUS: C4.1, C6.1, D7.4 (VCC), FB1.2, JP1.1 (A), R15.1, U3.1 (VIN)

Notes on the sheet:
Decoupling voltage MCU analog in
5V -> 3V3 regulator
Decoupling MCU voltage in
USB ESD protection
Decoupling capacitors
USB mini B connector with filtering
Decoupling voltage MCU IO in



Board: 4 copper layers, 56.1 x 51.6 mm, 79 parts (6 on the bottom side), 98 nets.

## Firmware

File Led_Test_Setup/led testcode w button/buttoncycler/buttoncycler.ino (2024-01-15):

// Simple demonstration on using an input device to trigger changes on your
// NeoPixels. Wire a momentary push button to connect from ground to a
// digital IO pin. When the button is pressed it will change to a new pixel
// animation. Initial state has all pixels off -- press the button once to
// start the first animation. As written, the button does not interrupt an
// animation in-progress, it works only when idle.

#include <Adafruit_NeoPixel.h>
#ifdef __AVR__
 #include <avr/power.h> // Required for 16 MHz Adafruit Trinket
#endif

// Digital IO pin connected to the button. This will be driven with a
// pull-up resistor so the switch pulls the pin to ground momentarily.
// On a high -> low transition the button press logic will execute.
#define BUTTON_PIN   60

#define PIXEL_PIN    A6  // Digital IO pin connected to the NeoPixels.

#define PIXEL_COUNT 1  // Number of NeoPixels

#define brightness A0
auto colorVal = 512;

// Declare our NeoPixel strip object:
Adafruit_NeoPixel strip(PIXEL_COUNT, PIXEL_PIN, NEO_GRB + NEO_KHZ800);
// Argument 1 = Number of pixels in NeoPixel strip
// Argument 2 = Arduino pin number (most are valid)
// Argument 3 = Pixel type flags, add together as needed:
//   NEO_KHZ800  800 KHz bitstream (most NeoPixel products w/WS2812 LEDs)
//   NEO_KHZ400  400 KHz (classic 'v1' (not v2) FLORA pixels, WS2811 drivers)
//   NEO_GRB     Pixels are wired for GRB bitstream (most NeoPixel products)
//   NEO_RGB     Pixels are wired for RGB bitstream (v1 FLORA pixels, not v2)
//   NEO_RGBW    Pixels are wired for RGBW bitstream (NeoPixel RGBW products)

boolean oldState = HIGH;
int     mode     = 0;    // Currently-active animation mode, 0-9

void setup() {
  pinMode(BUTTON_PIN, INPUT_PULLUP);
  pinMode(brightness, INPUT);
  strip.begin(); // Initialize NeoPixel strip object (REQUIRED)
  strip.show();  // Initialize all pixels to 'off'
}

void loop() {
  // Get current button state.
  boolean newState = digitalRead(BUTTON_PIN);
  colorVal = map(analogRead(brightness), 0, 1023, 0, 255);

  // Check if state changed from high to low (button press).
  if((newState == LOW) && (oldState == HIGH)) {
    // Short delay to debounce button.
    delay(20);
    // Check if button is still low after debounce.
    newState = digitalRead(BUTTON_PIN);
    if(newState == LOW) {      // Yes, still low
      if(++mode > 4) mode = 0; // Advance to next mode, wrap around after #8
      switch(mode) {           // Start the new animation...
        case 0:
          colorWipe(strip.Color(  0,   0,   0), 50);    // Black/off
          break;
        case 1:
          colorWipe(strip.Color(colorVal,   0,   0), 50);    // Red
          break;
        case 2:
          colorWipe(strip.Color(  0, colorVal,   0), 50);    // Green
          break;
        case 3:
          colorWipe(strip.Color(  0,   0, colorVal), 50);    // Blue
          break;
        case 4:
          colorWipe(strip.Color(  (colorVal/3), (colorVal/3), (colorVal/3)), 50);    // White
          // theaterChase(strip.Color(127, 127, 127), 50); // White
          break;
       // case 5:
       //   theaterChase(strip.Color(127,   0,   0), 50); // Red
       //   break;
       // case 6:
       //   theaterChase(strip.Color(  0,   0, 127), 50); // Blue
       //   break;
       // case 7:
       //   rainbow(10);
       //   break;
       // case 8:
       //   theaterChaseRainbow(50);
       //   break;
      }
    }
  }

  // Set the last-read button state to the old state.
  oldState = newState;
}

// Fill strip pixels one after another with a color. Strip is NOT cleared
// first; anything there will be covered pixel by pixel. Pass in color
// (as a single 'packed' 32-bit value, which you can get by calling
// strip.Color(red, green, blue) as shown in the loop() function above),
// and a delay time (in milliseconds) between pixels.
void colorWipe(uint32_t color, int wait) {
  for(int i=0; i<strip.numPixels(); i++) { // For each pixel in strip...
    strip.setPixelColor(i, color);         //  Set pixel's color (in RAM)
    strip.show();                          //  Update strip to match
    delay(wait);                           //  Pause for a moment
  }
}

// Theater-marquee-style chasing lights. Pass in a color (32-bit value,
// a la strip.Color(r,g,b) as mentioned above), and a delay time (in ms)
// between frames.
void theaterChase(uint32_t color, int wait) {
  for(int a=0; a<10; a++) {  // Repeat 10 times...
    for(int b=0; b<3; b++) { //  'b' counts from 0 to 2...
      strip.clear();         //   Set all pixels in RAM to 0 (off)
      // 'c' counts up from 'b' to end of strip in steps of 3...
      for(int c=b; c<strip.numPixels(); c += 3) {
        strip.setPixelColor(c, color); // Set pixel 'c' to value 'color'
      }
      strip.show(); // Update strip with new contents
      delay(wait);  // Pause for a moment
    }
  }
}

// Rainbow cycle along whole strip. Pass delay time (in ms) between frames.
void rainbow(int wait) {
  // Hue of first pixel runs 3 complete loops through the color wheel.
  // Color wheel has a range of 65536 but it's OK if we roll over, so
  // just count from 0 to 3*65536. Adding 256 to firstPixelHue each time
  // means we'll make 3*65536/256 = 768 passes through this outer loop:
  for(long firstPixelHue = 0; firstPixelHue < 3*65536; firstPixelHue += 256) {
    for(int i=0; i<strip.numPixels(); i++) { // For each pixel in strip...
      // Offset pixel hue by an amount to make one full revolution of the
      // color wheel (range of 65536) along the length of the strip
      // (strip.numPixels() steps):
      int pixelHue = firstPixelHue + (i * 65536L / strip.numPixels());
      // strip.ColorHSV() can take 1 or 3 arguments: a hue (0 to 65535) or
      // optionally add saturation and value (brightness) (each 0 to 255).
      // Here we're using just the single-argument hue variant. The result
      // is passed through strip.gamma32() to provide 'truer' colors
      // before assigning to each pixel:
      strip.setPixelColor(i, strip.gamma32(strip.ColorHSV(pixelHue)));
    }
    strip.show(); // Update strip with new contents
    delay(wait);  // Pause for a moment
  }
}

// Rainbow-enhanced theater marquee. Pass delay time (in ms) between frames.
void theaterChaseRainbow(int wait) {
  int firstPixelHue = 0;     // First pixel starts at red (hue 0)
  for(int a=0; a<30; a++) {  // Repeat 30 times...
    for(int b=0; b<3; b++) { //  'b' counts from 0 to 2...
      strip.clear();         //   Set all pixels in RAM to 0 (off)
      // 'c' counts up from 'b' to end of strip in increments of 3...
      for(int c=b; c<strip.numPixels(); c += 3) {
        // hue of pixel 'c' is offset by an amount to make one full
        // revolution of the color wheel (range 65536) along the length
        // of the strip (strip.numPixels() steps):
        int      hue   = firstPixelHue + c * 65536L / strip.numPixels();
        uint32_t color = strip.gamma32(strip.ColorHSV(hue)); // hue -> RGB
        strip.setPixelColor(c, color); // Set pixel 'c' to value 'color'
      }
      strip.show();                // Update strip with new contents
      delay(wait);                 // Pause for a moment
      firstPixelHue += 65536 / 90; // One cycle of color wheel over 90 frames
    }
  }
}

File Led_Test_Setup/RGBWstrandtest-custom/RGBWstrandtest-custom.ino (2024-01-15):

// NeoPixel test program showing use of the WHITE channel for RGBW
// pixels only (won't look correct on regular RGB NeoPixel strips).

#include <Adafruit_NeoPixel.h>
#ifdef __AVR__
 #include <avr/power.h> // Required for 16 MHz Adafruit Trinket
#endif

// Which pin on the Arduino is connected to the NeoPixels?
// On a Trinket or Gemma we suggest changing this to 1:
#define LED_PIN     A6

// How many NeoPixels are attached to the Arduino?
#define LED_COUNT  1

// NeoPixel brightness, 0 (min) to 255 (max)
#define BRIGHTNESS 50 // Set BRIGHTNESS to about 1/5 (max = 255)

// Declare our NeoPixel strip object:
Adafruit_NeoPixel strip(LED_COUNT, LED_PIN, NEO_GRBW + NEO_KHZ800);
// Argument 1 = Number of pixels in NeoPixel strip
// Argument 2 = Arduino pin number (most are valid)
// Argument 3 = Pixel type flags, add together as needed:
//   NEO_KHZ800  800 KHz bitstream (most NeoPixel products w/WS2812 LEDs)
//   NEO_KHZ400  400 KHz (classic 'v1' (not v2) FLORA pixels, WS2811 drivers)
//   NEO_GRB     Pixels are wired for GRB bitstream (most NeoPixel products)
//   NEO_RGB     Pixels are wired for RGB bitstream (v1 FLORA pixels, not v2)
//   NEO_RGBW    Pixels are wired for RGBW bitstream (NeoPixel RGBW products)

void setup() {
  // These lines are specifically to support the Adafruit Trinket 5V 16 MHz.
  // Any other board, you can remove this part (but no harm leaving it):
#if defined(__AVR_ATtiny85__) && (F_CPU == 16000000)
  clock_prescale_set(clock_div_1);
#endif
  // END of Trinket-specific code.

  strip.begin();           // INITIALIZE NeoPixel strip object (REQUIRED)
  strip.show();            // Turn OFF all pixels ASAP
  strip.setBrightness(BRIGHTNESS);
//  pinMode(5, OUTPUT);
//  pinMode(A0, OUTPUT);
}

void loop() {
//  digitalWrite(5, HIGH);   // turn the LED on (HIGH is the voltage level)
//  delay(1000);                       // wait for a second
//  digitalWrite(5, LOW);    // turn the LED off by making the voltage LOW
//  delay(1000);  
//  digitalWrite(A0, HIGH);   // turn the LED on (HIGH is the voltage level)
//  delay(1000);                       // wait for a second
//  digitalWrite(A0, LOW);    // turn the LED off by making the voltage LOW
//  delay(1000);  
  // Fill along the length of the strip in various colors...
//  colorWipe(strip.Color(255,   0,   0)     , 50); // Red
//  colorWipe(strip.Color(  0, 255,   0)     , 50); // Green
//  colorWipe(strip.Color(  0,   0, 255)     , 50); // Blue
//  colorWipe(strip.Color(  0,   0,   0, 255), 50); // True white (not RGB white)
//
//  whiteOverRainbow(75, 5);
//
//  pulseWhite(5);
//
  rainbowFade2White(3, 3, 1);
}

// Fill strip pixels one after another with a color. Strip is NOT cleared
// first; anything there will be covered pixel by pixel. Pass in color
// (as a single 'packed' 32-bit value, which you can get by calling
// strip.Color(red, green, blue) as shown in the loop() function above),
// and a delay time (in milliseconds) between pixels.
void colorWipe(uint32_t color, int wait) {
  for(int i=0; i<strip.numPixels(); i++) { // For each pixel in strip...
    strip.setPixelColor(i, color);         //  Set pixel's color (in RAM)
    strip.show();                          //  Update strip to match
    delay(wait);                           //  Pause for a moment
  }
}

void whiteOverRainbow(int whiteSpeed, int whiteLength) {

  if(whiteLength >= strip.numPixels()) whiteLength = strip.numPixels() - 1;

  int      head          = whiteLength - 1;
  int      tail          = 0;
  int      loops         = 3;
  int      loopNum       = 0;
  uint32_t lastTime      = millis();
  uint32_t firstPixelHue = 0;

  for(;;) { // Repeat forever (or until a 'break' or 'return')
    for(int i=0; i<strip.numPixels(); i++) {  // For each pixel in strip...
      if(((i >= tail) && (i <= head)) ||      //  If between head & tail...
         ((tail > head) && ((i >= tail) || (i <= head)))) {
        strip.setPixelColor(i, strip.Color(0, 0, 0, 255)); // Set white
      } else {                                             // else set rainbow
        int pixelHue = firstPixelHue + (i * 65536L / strip.numPixels());
        strip.setPixelColor(i, strip.gamma32(strip.ColorHSV(pixelHue)));
      }
    }

    strip.show(); // Update strip with new contents
    // There's no delay here, it just runs full-tilt until the timer and
    // counter combination below runs out.

    firstPixelHue += 40; // Advance just a little along the color wheel

    if((millis() - lastTime) > whiteSpeed) { // Time to update head/tail?
      if(++head >= strip.numPixels()) {      // Advance head, wrap around
        head = 0;
        if(++loopNum >= loops) return;
      }
      if(++tail >= strip.numPixels()) {      // Advance tail, wrap around
        tail = 0;
      }
      lastTime = millis();                   // Save time of last movement
    }
  }
}

void pulseWhite(uint8_t wait) {
  for(int j=0; j<256; j++) { // Ramp up from 0 to 255
    // Fill entire strip with white at gamma-corrected brightness level 'j':
    strip.fill(strip.Color(0, 0, 0, strip.gamma8(j)));
    strip.show();
    delay(wait);
  }

  for(int j=255; j>=0; j--) { // Ramp down from 255 to 0
    strip.fill(strip.Color(0, 0, 0, strip.gamma8(j)));
    strip.show();
    delay(wait);
  }
}

void rainbowFade2White(int wait, int rainbowLoops, int whiteLoops) {
  int fadeVal=0, fadeMax=100;

  // Hue of first pixel runs 'rainbowLoops' complete loops through the color
  // wheel. Color wheel has a range of 65536 but it's OK if we roll over, so
  // just count from 0 to rainbowLoops*65536, using steps of 256 so we
  // advance around the wheel at a decent clip.
  for(uint32_t firstPixelHue = 0; firstPixelHue < rainbowLoops*65536;
    firstPixelHue += 256) {

    for(int i=0; i<strip.numPixels(); i++) { // For each pixel in strip...

      // Offset pixel hue by an amount to make one full revolution of the
      // color wheel (range of 65536) along the length of the strip
      // (strip.numPixels() steps):
      uint32_t pixelHue = firstPixelHue + (i * 65536L / strip.numPixels());

      // strip.ColorHSV() can take 1 or 3 arguments: a hue (0 to 65535) or
      // optionally add saturation and value (brightness) (each 0 to 255).
      // Here we're using just the three-argument variant, though the
      // second value (saturation) is a constant 255.
      strip.setPixelColor(i, strip.gamma32(strip.ColorHSV(pixelHue, 255,
        255 * fadeVal / fadeMax)));
    }

    strip.show();
    delay(wait);

    if(firstPixelHue < 65536) {                              // First loop,
      if(fadeVal < fadeMax) fadeVal++;                       // fade in
    } else if(firstPixelHue >= ((rainbowLoops-1) * 65536)) { // Last loop,
      if(fadeVal > 0) fadeVal--;                             // fade out
    } else {
      fadeVal = fadeMax; // Interim loop, make sure fade is at max
    }
  }

  for(int k=0; k<whiteLoops; k++) {
    for(int j=0; j<256; j++) { // Ramp up 0 to 255
      // Fill entire strip with white at gamma-corrected brightness level 'j':
      strip.fill(strip.Color(0, 0, 0, strip.gamma8(j)));
      strip.show();
    }
    delay(1000); // Pause 1 second
    for(int j=255; j>=0; j--) { // Ramp down 255 to 0
      strip.fill(strip.Color(0, 0, 0, strip.gamma8(j)));
      strip.show();
    }
  }

  //delay(500); // Pause 1/2 second
}
